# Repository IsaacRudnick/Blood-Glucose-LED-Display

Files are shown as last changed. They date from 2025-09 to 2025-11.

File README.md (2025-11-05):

# Blood Glucose Display Matrix

This is a complete project for a 32x8 RGB LED matrix display using an ESP32 microcontroller. The project includes hardware design files for the physical enclosure, assembly instructions, and microcontroller code for driving the display. Though this project was originally designed to show blood glucose data from a Nightscout API, it can be modified to display anything you want, and you can use the enclosure alone without my code if desired.

## Coming Soon

- Proper pictures
- 3D Print tolerance improvements
- Better diffuser grid to eliminate pixel bleed
- More modular design

## Features

- **Real-Time Blood Glucose Display:** Continuously fetches and displays the latest blood glucose readings from a Nightscout API.
- **LED Matrix Visualization:** Shows readings, delta (change), and a progress bar on a 32x8 WS2812B LED matrix using a modifiable 4x6 pixel font.
- **Color-Coded Alerts:** Readings are color-coded (green, orange, red) to indicate normal, warning, or critical glucose levels.
- **Day/Night Brightness:** Automatically adjusts LED brightness for day and night to reduce glare and save power.
- **Wi-Fi and HTTP Error Handling:** Shows error messages on the display if Wi-Fi or API connection fails.
- **Progress Bar:** Visualizes time since last reading with a dynamic progress bar, adapting its style for day and night.
- **Old Data Warning:** Alerts if the displayed data is outdated.
- **Configurable Settings:** Easily adjust brightness, day/night hours, and data refresh intervals in `Settings.h`.
- **3D Printable Enclosure:** Custom-designed 3D-printable enclosure files to aid in light diffusion.

## Bill of Materials

This project requires access to a 3D printer if you want to create the enclosure, but the display can be used without it.
Unique items. In the "Required" column, "Y" means it is necessary and "N" means it is only needed if you want to build the enclosure.

| Required | Quantity | Part                                                                | Approx. Price (USD) |
| -------- | -------- | ------------------------------------------------------------------- | ------------------- |
| Y        | 1        | ESP32 Development Board                                             | ~$8                 |
| Y        | 1        | [32x8 WS2812B RGB LED Matrix](https://www.amazon.com/dp/B07P5TSKX8) | ~$15                |
|          |          |                                                                     |                     |
| N        | ~1kg     | PLA or PETG\*                                                       | ~15                 |
| N        | 1        | [Display Power Button](https://www.amazon.com/dp/B0D55TLT1K)        | ~$9/pack            |
| N        | 1        | [USB-C Jack](https://www.amazon.com/dp/B0D17K3CCY)                  | $13                 |
| N        | 1        | [Mylar Sheet\*\*](https://www.amazon.com/dp/B09BJTT6JH)             | ~$17/pack           |

> \* I used RAPID PETG for the enclosure and bowties. I used generic PLA for the other parts. I reccomend a different color of filament for the bowties if you want an accent color.

> \*\*Mylar sheet looks the best, but it can be replaced with any thin light-diffusing material. I have not tried with wax or parchment paper, but it may work. You can also try printing a thin sheet of white or clear PLA (or modifying the "Upper" grid part to have a thin solid layer at the top).

You will also need a breadboard and some jumper wires for wiring this up. A soldering iron is recommended for making more permanent connections. Many makerspaces have these available for very cheap if you do not own them.

## Assembly Instructions

### Software Setup

1. Install [Visual Studio Code](https://code.visualstudio.com/).
1. Install the [PlatformIO IDE extension](https://platformio.org/install/ide?install=vscode).
1. Open the project folder in Visual Studio Code.
1. Create a `Secrets.h` file in the `include` directory using the `ExampleSecrets.h` file as a template.
1. Connect the ESP32 to your computer via USB. If PlatformIO does not automatically detect the serial port, you may need to install the appropriate USB drivers for your ESP32 board. These worked for me:
   - [CP210x USB to UART Bridge VCP Drivers](https://www.silabs.com/software-and-tools/usb-to-uart-bridge-vcp-drivers?tab=downloads)
1. Wire up the ESP32 to the LED matrix as shown in the wiring diagram below. Do not permanently wire the power switch until it is installed in the enclosure. It is recommended to use a connector of some sort so the power switch can be disconnected if needed.
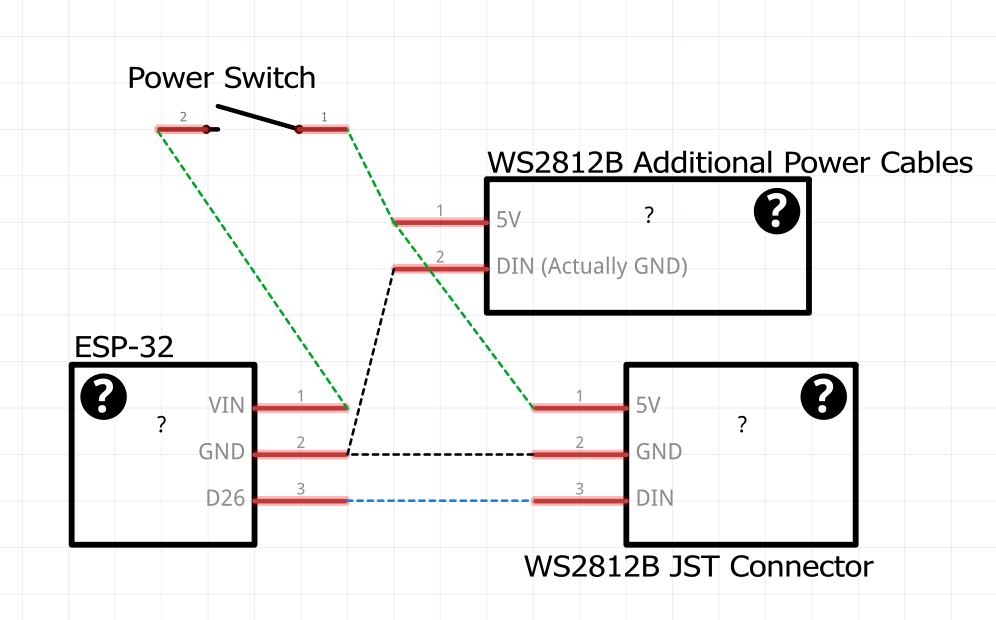
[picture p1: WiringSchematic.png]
Wiring Diagram
   

   > To connect the JST connector's wires to the breadboard, you should strip them and add dupont connectors.

   > Note that the WS2812B matrix's _middle_ wires are labeled "5V" and "DIN" but **the middle "DIN" wire is actually GND**.

1. Upload the code to the ESP32 using PlatformIO. Use the "Upload and Monitor" option to see serial output for debugging.
1. Once uploaded, the ESP32 should connect to Wi-Fi and start displaying data on the LED matrix. If you encounter any issues, check the serial monitor for error messages.

If this works, continue to the hardware assembly instructions below.

### Hardware Assembly

1. 3D print the enclosure parts using the provided 3mf files in the [print-files](./print-files/) directory:

   | Quantity | Filename           | Notes                                                                                                                                 |
   | -------- | ------------------ | ------------------------------------------------------------------------------------------------------------------------------------- |
   | 1        | `SupportPlate.3mf` | Print in any color. This is entirely internal.                                                                                        |
   | 1        | `Grid.3mf`         | Print the bodies named "Lower" in white; they help with light diffusion. Print the bodies named "Upper" in your main (shell's) color. |
   | 3        | `Bowtie.3mf`       | Highly recommend high infill and an accent color if desired.                                                                          |
   | 1        | `Shell.3mf`        | Recommend high infill. This is the outermost and largest part of the assembly.                                                        |

2. Assemble the enclosure as follows:

- The display power button switch goes in the small hole on the top of the shell. The USB-C port jack goes through the larger hole in the back of the shell. The ESP32 goes loosely inside the shell, so a soldered connection for the wires is recommended.
- The SupportPlate sits behind the LED matrix.
- On top of the LED matrix is the bottom of the grid.
- On top of that is a thin sheet of mylar to help with light diffusion. Cut this to size using the bottom grid piece as a template. It can be slightly smaller than the grid piece, but not larger.
- On top of that is the upper part of the grid. The shell goes around everything, and the bowties hold the shell together.

Finally, the bowties go in the recesses in the shell to hold everything together. The bowties should snap tightly into place. If they are too tight, a small amount of filing or sanding can help.

> A small scraping or filing tool can help manually increase tolerances if needed.

> If the assembly does not fit together, verify that there are no wires blocking closure between the halves. It is possible that the assembly around the matrix is not fitting all the way into the groove at one or both ends of the shell halves. Sometimes a small amount of filing or sanding can help. All components in a half (shell, plate, grid bottom and top) should sit flush with the outer edge of the shell half. Assembly can be tricky. Try getting one half slotted in first, then add the other half.

## Troubleshooting

- If the ESP32 does not connect to Wi-Fi, double-check the SSID and password in `Secrets.h`.
- If the LED matrix does not display anything, ensure that the wiring matches the diagram and that the matrix is powered correctly. Your USB-C cable may not provide enough power; try a different cable or power source.
- If the display is dim or colors are inaccurate, check the brightness settings in `Settings.h`. Brightness below 3 can compromise color accuracy.

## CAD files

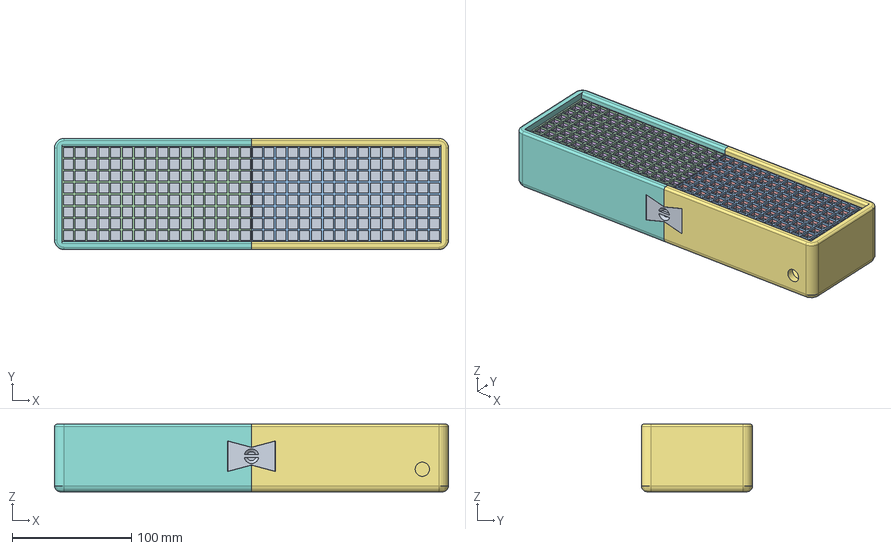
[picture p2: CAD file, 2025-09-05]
CAD-files/Generic-CAD-Files.step
331.0 x 93.5 x 56.9 mm
Matrix
SupportPlate
Upper
Lower
Bowtie x 3

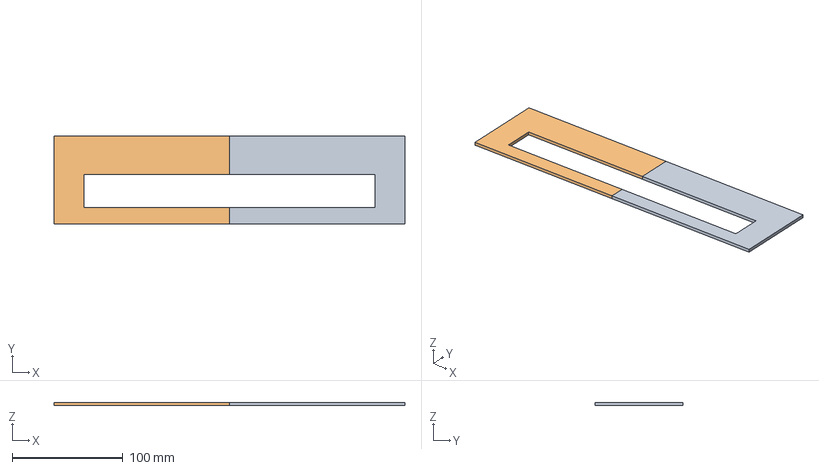
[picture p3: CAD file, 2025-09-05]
print-files/SupportPlate.3mf
317.5 x 80.0 x 3.00 mm

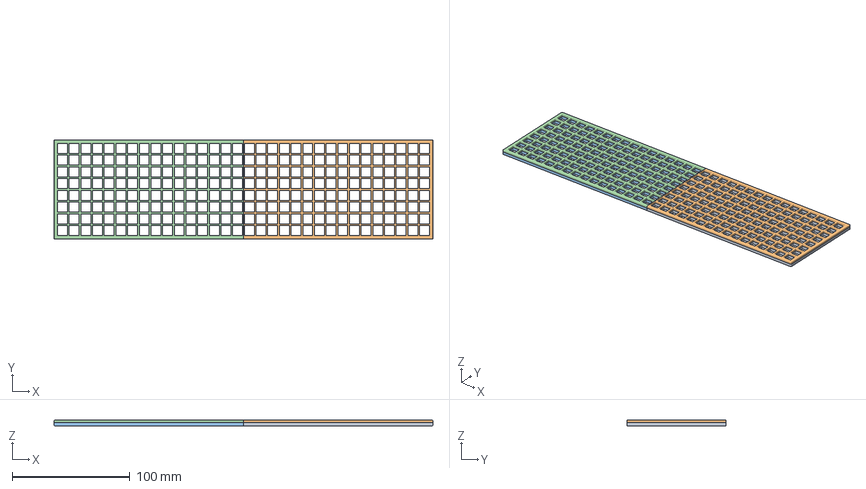
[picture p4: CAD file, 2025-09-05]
print-files/Grid.3mf
322.0 x 84.5 x 4.75 mm

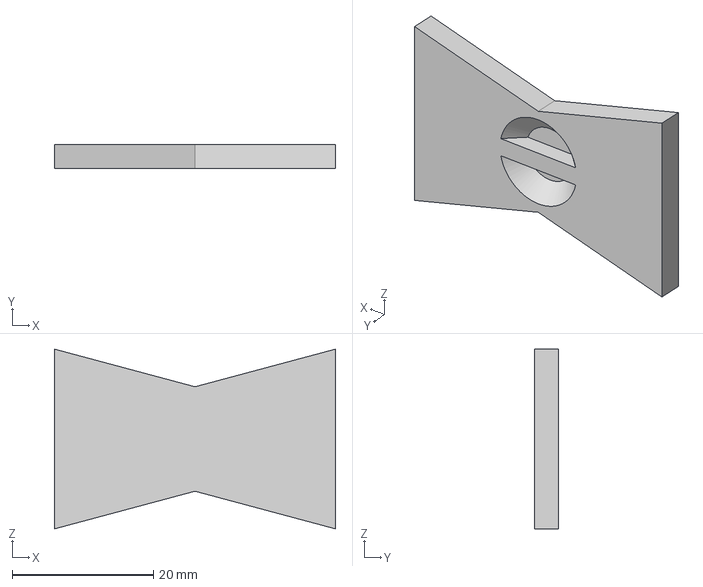
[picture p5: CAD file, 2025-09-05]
print-files/Bowtie.3mf
39.8 x 3.40 x 25.5 mm

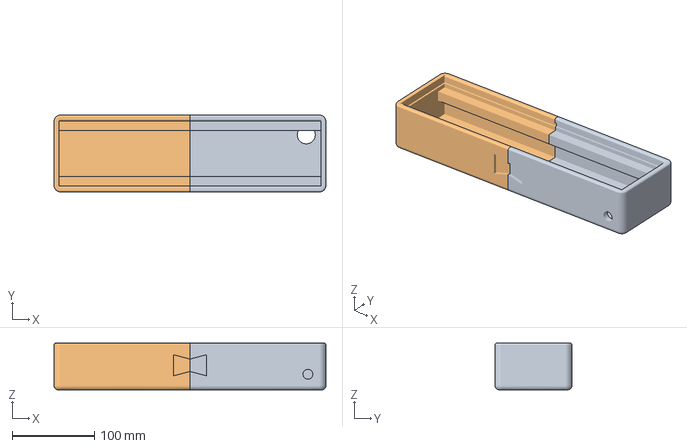
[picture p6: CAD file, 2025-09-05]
print-files/Shell.3mf
331.0 x 93.5 x 56.9 mm

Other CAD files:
CAD-files/Fusion360-Source.f3d

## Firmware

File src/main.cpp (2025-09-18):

#include <FastLED.h>
#include <WiFi.h>
#include <WiFiUdp.h>
#include <NTPClient.h>
#include <WiFiClientSecure.h>
#include <ArduinoHTTPClient.h>
#include <ArduinoJson.h>
#include "font4x6.h"
#include "Secrets.h"
#include "Settings.h"

// LED Matrix Configuration
#define LED_DATA_PIN 26
#define LED_COUNT (8 * 32)
#define WIDTH 32
#define HEIGHT 8

CRGB leds[LED_COUNT];

// NTP Client setup
WiFiUDP ntpUDP;
NTPClient timeClient(ntpUDP, "pool.ntp.org", 0, 60 * 1000); // UTC timezone, update every 60s

WiFiClientSecure wifiClient;
HttpClient client(wifiClient, serverName, port);

bool isDayTime()
{
  int currentHour = timeClient.getHours();
  // Account for the fact that night_start_hour might be after midnight
  if (DAY_START_HOUR < NIGHT_START_HOUR)
  {
    return (currentHour >= DAY_START_HOUR && currentHour < NIGHT_START_HOUR);
  }
  else
  {
    return (currentHour >= DAY_START_HOUR || currentHour < NIGHT_START_HOUR);
  }
}

void setMaxBrightnessFromTime()
{
  if (isDayTime())
  {
    FastLED.setBrightness(DAY_BRIGHTNESS);
  }
  else
  {
    FastLED.setBrightness(NIGHT_BRIGHTNESS); // Nighttime brightness
  }
}

// Map 2D coords to LED index for your matrix layout
// Zero-based indexing: (0,0) is bottom-left, (31,7) is top-right
int mapXYtoIndex(int x, int y)
{
  // Subtract 1 for 0-based indexing
  int colFromRight = WIDTH - 1 - x;
  int colStart = colFromRight * HEIGHT;
  // Serpentine layout, so reverse every other column
  bool isEvenCol = (colFromRight % 2 == 0);
  if (isEvenCol)
  {
    return colStart + y; // Even column: bottom → top
  }
  else
  {
    // Subtract 1 for 0-based indexing
    return colStart + (HEIGHT - 1 - y); // Odd column: top → bottom
  }
}

// Draw a single 4x6 character from font4x6
void drawChar(char c, int x, int yTop, CRGB color)
{
  if (c < 32)
    return; // Only printable chars supported

  int charIndex = (c - 32) * 6; // Each char uses 6 bytes (rows), though the last 3 are empty.
  int width = font4x6[0];
  int height = font4x6[1];

  for (int row = 0; row < height; row++)
  {
    if (yTop + row >= HEIGHT || yTop + row < 0)
      continue;
    uint8_t rowBits = font4x6[3 + charIndex + row]; // byte for this row
    for (int col = 0; col < width; col++)
    {
      if (x + col < 0 || x + col >= WIDTH)
        continue;
      // Bit 7 = leftmost pixel, bit 4 = rightmost pixel (since font bits are left aligned)
      // Our font is stored MSB to LSB left to right, so test bit 7-col
      if (rowBits & (0x80 >> col))
      {
        int px = x + col;
        int py = (HEIGHT - 1) - (yTop + row); // flip vertical for LED indexing

        // Subtract 1 from y to lower the visual by 1 pixel. This is optional.
        py -= 1;
        leds[mapXYtoIndex(px, py)] = color;
      }
    }
  }
}

// Draw a string horizontally with 1 pixel spacing (4 pixels per char)
void drawString(const char *str, int xStart, int yTop, CRGB color)
{
  int x = xStart;
  for (int i = 0; str[i] != '\0'; i++)
  {
    if (str[i] == ' ')
    {
      x += 2; // space width smaller (2 pixels)
      continue;
    }
    drawChar(str[i], x, yTop, color);
    // Move cursor to the right by 4, since font is 4 pixels wide (spaces are built in)
    x += 4;
  }
}

void displayError(const char *message)
{
  FastLED.clear();
  drawString((char *)message, 1, 1, CRGB::Red);
  FastLED.show();
}

// Draw bottom row progress bar (y=0)
void drawProgressBar(int elapsedTimeSeconds, int maxTimeSeconds)
{
  int barLength = map(elapsedTimeSeconds, 0, maxTimeSeconds, 0, WIDTH - 1);
  barLength = constrain(barLength, 0, WIDTH - 1);

  // Clear bottom row
  for (int x = 0; x < WIDTH; x++)
  {
    leds[mapXYtoIndex(x, 0)] = CRGB::Black;
  }

  // Daytime progress bar is bottom row filling up from left to right in white
  if (isDayTime())
  {
    for (int x = 0; x < barLength; x++)
    {
      leds[mapXYtoIndex(x, 0)] = CRGB::White;
    }
    return;
  }
  // Modify color logic here (for progress bar)
  // Nighttime progress bar is a single pixel (head of progress bar) moving from left to right.
  // There's also a start and end pixel in blue for visual reference.

  // First and last pixel of bottom row in blue
  leds[mapXYtoIndex(0, 0)] = CRGB::DarkBlue;
  leds[mapXYtoIndex(WIDTH - 1, 0)] = CRGB::DarkBlue;
  // Last pixel of progress bar in white
  leds[mapXYtoIndex(barLength - 1, 0)] = CRGB::White;
}

CRGB getColorForValue(int value)
{
  // Modify color logic here
  // This is the default color for in-range values
  CRGB color = CRGB::Green;
  // If value is beyond critical threshold, show red
  if (value < CRITICAL_LOW_THRESHOLD || value > CRITICAL_HIGH_THRESHOLD)
  {
    color = CRGB::Red;
  }
  // If value is beyond moderate threshold, show orange
  else if (value < MODERATE_LOW_THRESHOLD || value > MODERATE_HIGH_THRESHOLD)
  {
    color = CRGB(255, 140, 0); // Orange
  }
  return color;
}

// Display value, delta and progress bar
void updateDisplay(int value, int delta, int elapsedSeconds)
{
  FastLED.clear();

  CRGB color = getColorForValue(value);

  // If value is beyond critical threshold, show red
  if (value < CRITICAL_LOW_THRESHOLD || value > CRITICAL_HIGH_THRESHOLD)
  {
    color = CRGB::Red;
  }
  // If value is beyond moderate threshold, show orange
  else if (value < MODERATE_LOW_THRESHOLD || value > MODERATE_HIGH_THRESHOLD)
  {
    color = CRGB(255, 140, 0); // Orange
  }
  // This is the end of the color function

  char displayStr[12];
  snprintf(displayStr, sizeof(displayStr), " %d %c%d", value, (delta >= 0 ? '+' : '-'), abs(delta));

  drawString(displayStr, 0, 0, color);

  drawProgressBar(elapsedSeconds, SECONDS_BETWEEN_READINGS);

  FastLED.show();
}

// ==================== BOOT ANIMATIONS ====================

// 2. White pixel animation
void bootWhitePixel()
{
  const int tailLength = 8;  // length of the white snake
  const int speedDelay = 30; // delay between frames in ms

  FastLED.clear();

  for (int pos = 0; pos < WIDTH + tailLength; pos++)
  {
    FastLED.clear();

    for (int t = 0; t < tailLength; t++)
    {
      int x = pos - t;
      if (x >= 0 && x < WIDTH)
      {
        // Tail brightness decreases from head to tail
        uint8_t brightness = 255 * (tailLength - t) / tailLength;

        for (int y = 0; y < HEIGHT; y++)
        {
          leds[mapXYtoIndex(x, y)] = CRGB(brightness, brightness, brightness);
        }
      }
    }

    FastLED.show();
    delay(speedDelay);
  }
}

// 3. Rainbow wave
void bootRainbowWave(uint16_t duration_ms = 3000)
{
  uint32_t startTime = millis();
  float offset = 0.0;
  while (millis() - startTime < duration_ms)
  {
    for (uint8_t y = 0; y < HEIGHT; y++)
    {
      for (uint8_t x = 0; x < WIDTH; x++)
      {
        float wave = sinf((x + offset) * 0.3) + cosf((y + offset) * 0.3);
        uint8_t hue = (wave * 40) + 128;
        leds[mapXYtoIndex(x, y)] = CHSV(hue, 255, 255);
      }
    }
    FastLED.show();
    offset += 0.2;
    delay(20);
  }
  FastLED.clear();
  FastLED.show();
}

void runBootSequence()
{
  bootWhitePixel();
  bootRainbowWave();
}

void setup()
{
  Serial.begin(9600);
  delay(100);

  // If LED matrix is using wrong color order, change GRB to RGB or BRG
  FastLED.addLeds<WS2812B, LED_DATA_PIN, GRB>(leds, LED_COUNT);
  // We don't have the time yet, so this will set to the daytime brightness.
  setMaxBrightnessFromTime();
  FastLED.clear();
  FastLED.show();
  runBootSequence();

  Serial.print("Connecting to ");
  Serial.println(ssid);
  WiFi.begin(ssid, password);

  FastLED.clear();
  drawString("WAITWIFI", 0, 1, CRGB::White);
  FastLED.show();
  WiFi.waitForConnectResult(WIFI_CONNECT_TIMEOUT_MS);

  if (WiFi.status() != WL_CONNECTED)
  {
    Serial.println("Failed to connect to Wi-Fi");
    // Print "WIFI ERR" to display
    displayError("WIFI ERR");
  }
  else
  {
    Serial.println("Wi-Fi connected");
    FastLED.clear();
    drawString("WAITDATA", 0, 1, CRGB::White);
    FastLED.show();
  }

  // Start an NTP client for accurate UNIX time
  timeClient.begin();
  timeClient.update();

  // Wait for time to be set
  client.setHttpResponseTimeout(HTTP_REQUEST_TIMEOUT_MS);
  // Skip https certificate validation
  wifiClient.setInsecure();
}

struct Reading
{
  unsigned long epoch = 0;
  int value = 0;
  int delta = 0;
};

Reading lastReading;

bool ensureWiFi()
{
  if (WiFi.status() == WL_CONNECTED)
    return true;

  WiFi.reconnect();
  Serial.println("Wifi disconnected. Reconnecting...");
  displayError("WIFI ERR");
  return false;
}

// Url is string + apiToken
const String url = String("/api/v2/entries.json?count=2&token=") + apiToken;

// Fetch the latest reading from the API
// Returns true if successful, false otherwise.
// Handles display of errors.
bool fetchLatestReading()
{
  Serial.print("Making request: ");
  Serial.println(url);

  client.get(url);
  int statusCode = client.responseStatusCode();
  String response = client.responseBody();

  if (statusCode != 200)
  {
    Serial.printf("HTTP Error: %d\n", statusCode);
    Serial.println("Response: " + response);
    displayError("HTTP ERR");
    WiFi.reconnect();
    WiFi.waitForConnectResult(WIFI_CONNECT_TIMEOUT_MS);
    return false;
  }

  JsonDocument doc;
  DeserializationError err = deserializeJson(doc, response);
  if (err)
  {
    Serial.print("JSON parse error: ");
    Serial.println(err.c_str());
    displayError("JSON ERR");
    return false;
  }

  int mostRecentValue = doc[0]["sgv"];
  unsigned long mostRecentDate = doc[0]["date"].as<unsigned long long>() / 1000;
  int previousValue = doc[1]["sgv"];
  int delta = mostRecentValue - previousValue;

  lastReading.epoch = mostRecentDate;
  lastReading.value = mostRecentValue;
  lastReading.delta = delta;

  Serial.printf("Most recent value: %d\n", mostRecentValue);
  Serial.printf("Delta: %d\n", delta);

  return true;
}

void loop()
{
  // If WiFi is disconnected and we can't reconnect, skip the rest of the loop.
  // ensureWiFi will display an error and return false if it fails.
  if (!ensureWiFi())
  {
    return;
  }

  timeClient.update();
  setMaxBrightnessFromTime();

  unsigned long currentEpoch = timeClient.getEpochTime();
  // If we have no previous reading, or it's been a long time, fetch a new one.
  int secondsSinceLastReading = (lastReading.epoch > 0)
                                    ? (int)(currentEpoch - lastReading.epoch)
                                    : INT_MAX; // INT_MAX so that we always fetch on the first run

  // If we expect a new reading within START_FETCHING_EARLY_SECONDS, start trying to fetch one.
  if (secondsSinceLastReading >= SECONDS_BETWEEN_READINGS - START_FETCHING_EARLY_SECONDS)
  {
    Serial.println("Fetching new reading...");
    // If fetchLatestReading fails, exit the loop and try again later.
    // fetchLatestReading will display an error and return false if it fails.
    if (!fetchLatestReading())
    {
      return;
    }
    // fetchLatestReading updates lastReading on success. If it failed, we keep the old reading.
    // Thus, we will get the correct secondsSinceLastReading regardless of success or failure of getting a new reading.
    secondsSinceLastReading = (lastReading.epoch > 0)
                                  ? (int)(currentEpoch - lastReading.epoch)
                                  : INT_MAX;
  }

  // If the last reading is too old, show an error.
  if (secondsSinceLastReading > OLD_DATA_THRESHOLD_SECONDS)
  {
    displayError("OLD DATA");
    // This will cause the next loop to try fetching again.
    return;
  }

  // For 5 seconds, display the value, delta and progress bar.
  // This lets us avoid making too many HTTP requests too quickly.
  unsigned long start = millis();
  // This is a loop instead of a single updateDisplay call so that the progress bar updates over time.
  while (millis() - start < SECONDS_BETWEEN_FETCHES * 1000)
  {
    updateDisplay(lastReading.value, lastReading.delta, secondsSinceLastReading);
    delay(100);
  }
}

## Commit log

2025-09-05 First commit. Working product.
    [Bowtie.3mf, Fusion360-Source.f3d, Generic-CAD-Files.step, Grid.3mf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]
2025-09-05 Add assembly instructions
2025-09-05 Add detailed Bill of Materials section to README
2025-09-05 Update Bill of Materials description
    Removed the optional recommendation note from the Bill of Materials section.
